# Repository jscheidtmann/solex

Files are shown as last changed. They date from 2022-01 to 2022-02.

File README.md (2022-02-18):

# Build Report for a Sol'ex Spectroheliograph
by Jens Scheidtmann

## Introduction
Christian Buit created a Do-It-Yourself 3D-print spectroheliograph, see its presentation and build instructions here:
http://www.astrosurf.com/solex/sol-ex-presentation-en.html. 

This build-log reports on my attempt at building it in the form of a diary. I hope this will be useful for others, so that my 
experience will help others. 

### License

This work is licensed under the Creative Commons Attribution-ShareAlike 4.0 International License. See file LICENSE for details.

## Building the Sol'ex

### 2022-01-12
The Shelyak kit arrived: Got the lenses, the diffraction grating, the slit and additional items for building a Star'ex. 
It's the [kit from Shelyak](https://www.shelyak.com/produit/es0027-solex-and-starex-optical-kit/?lang=en).

M3 and M4 Screws are on the way. I ordered sets of M3 and M4 screws from 4 mm length up to 40 mm length and some 
additional larger washers. Mold insert nuts are M3 and M4 from Ruthex. Unfortunately I couldn't find a bill of material 
on the original site.   

Hopefully one roll of PETG
[black filament from dasfilament](https://www.dasfilament.de/filament-spulen/petg-1-75-mm/158/petg-filament-1-75-mm-schwarz?c=21) 
is enough.

Note: Later on it turned out that a two 50mm M4 screws are necessary. 

### 2022-01-13
Read the DADOS Tutorials by [Bernd Koch](http://astrofoto.de/german/profil/fprofil.htm) available [here](https://www.baader-planetarium.com/de/blog/neue-tutorials-fuer-den-dados-spaltspektrografen/) on Baader's site (in German, english version available [here](https://www.unitronitalia.com/schede/Baader-Dados-tutorial.pdf - very slow download). Ordered a MegaMan lamp for callibration purposes.

### 2022-01-14
Ordered two [helical ZWO focusers](https://www.astroshop.eu/focusers/zwo-helical-focuser-1-25-/p,63166) and a T2-1.25" adapter.

### 2022-01-16
Conducted first prints with the PETG filament on a Flashforge Finder. The PETG is much more prone to warping, i.e. a raft and 
glue is mandatory. Hopefully I can print the large spectrometre body parts with-out too much warping.

These are the settings I used in FlashPrint 5.2.1: 
 - Extruder Temp: 230°C
 - Shells: 3
 - Infill: 60%
 - Infull-Type: Hexagons
 - Activate Raft: Yes  (used the other default settings) 

Today's printed parts (named as given in [this picture](http://www.astrosurf.com/solex/images/image-collee-701-1.webp)):
 - Interface tel. #1 (My T2-1.25" adapter fits snuggly, even on the first warped print)
 - Support fente #2
 - Bague collimateur #5
 - Support réseau #9
 - Patte réseau #10
 - Bague objective #11
 - Bague épaisseur #13
 - Raidisseur #14

Here's a picture of the parts:

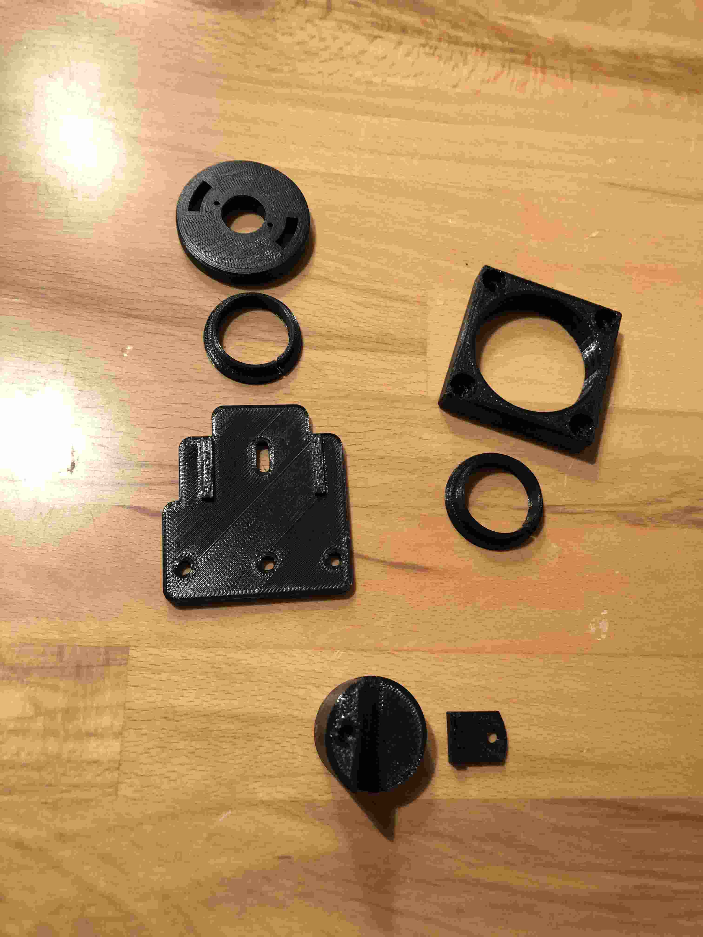
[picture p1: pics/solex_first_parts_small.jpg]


We will see, if I need to reprint the rings (#5 and #11) as they have a little bit of warping.

The STL-files are [available on github](https://github.com/Vdesnoux/Sol-ex) and there are some extensions available in subdirs:
 - motorisation_fichiers, move the diffraction grating with a motor
 - cache_parasite, avoid scattered light in the sprectrometre body
 - vernier_reseau, a dial for more visually selecting the color that is centered in the cam. Couldn't find the print-out for that, yet.

There is also a mailing list (french mostly): https://groups.io/g/Solex-project, on which new developments/extensions are reported.

### 2022-01-17
Printing the upper body part. Unfortunately this large element experienced some warping. Fortunately, the body is large enough, so that the optical path is not affected by the warping. 

### 2022-01-18
Printing the lower body part. I made especially sure that a good layer of glue is present on the 3D-printing bed. 4 hours into the printing, one edge of the body had disconnected from the bed and warping developed, which is similar to the upper body part printed yesterday. Hopefully I am able to account for the warping with the screws. If needed, I will have to print something so that the "Radisseur" (stiffener) plate is at its expected position. 

Here are pictures of both parts, so you can see the warping:

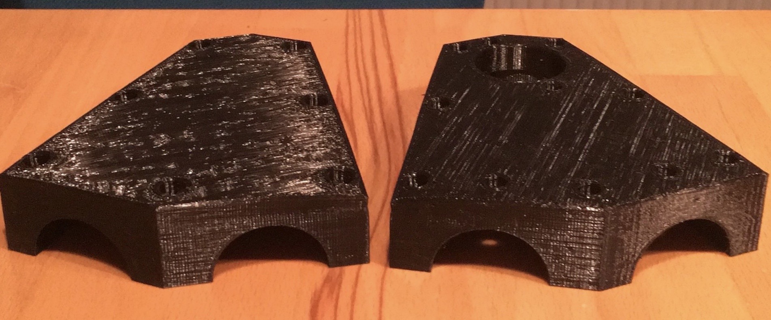
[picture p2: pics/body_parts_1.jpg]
Picture of body parts with warping ()
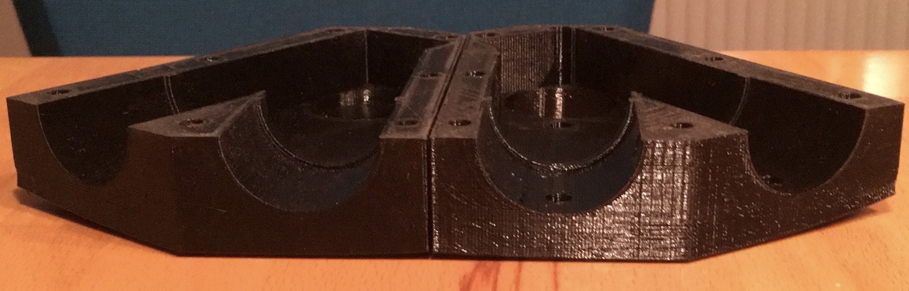
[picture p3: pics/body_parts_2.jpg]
Picture of body parts with warping ()
  

### 2022-01-19
Printed the two tubes (#4 and #12) and the collimator block (#3). The helical focusers and the T2-adapter arrived. Now everything is there to finish the Sol-ex.

The grating holder did not fit into the body part, so I had to sand the opening and the grating holder. I also sanded the body parts where they are in contact, in order get a tight fit. The T2-adapter fits nicely into the interface (#1). I printed it with-out raft (and it had no warping) and with normal layer thickness.

So far I was unable to fit the focuser on the respective tube (#12). I should have printed it in "fine" setting, but did use the normal setting, as the T2 adapter fitted perfectly in part #1. The problem is that the tube-thread does not grip the thread in the focuser. Or when it does, it's only one side of the tube and the tube gets stuck after a couple of degrees. I will reprint this one using "fine" layer thickness and probably use another slicer that randomizes the start point of outer layers. Hopefully this will be finished tomorrow. I will not use a raft, but then may have some elefant foot, which I should be able to cure with a bit of sanding.

Using the candle method I installed all Ruthex M4 and M3 threaded inserts in the body parts. A few seconds in the candle was enough. 
Some screws in the area where warping occurred could not be pushed fully in. As the screws are anyway pulling them further in, probably no problem. 

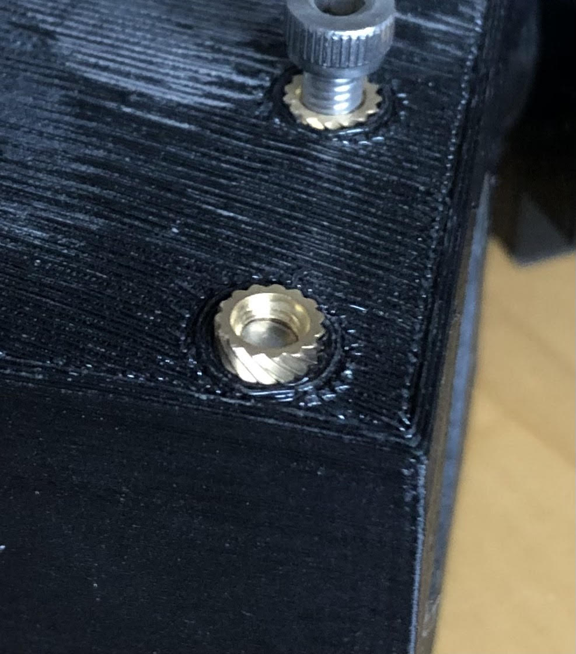
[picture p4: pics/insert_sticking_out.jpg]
Threaded insert sticking out


The collimator block needs a tad more sanding on the telescope side, as a slight warping is present. I also need to sand the tube to make it fit in the openinig of the collimator block. The slit holder will need the same treatment. 

Assembled the grating. The holder is a snug fit for the grating: I had to apply quite some force to fully place it on the holder.
I had to press a bit to get it down all the way.

### 2022-01-20
Printed the tube for the camera end: no raft, fine layer setting. Did not randomize start points.
I tried to print the disk to rotate the grating (#8). Unfortunately the infill set-up has been destroyed (or there's a bug in the slicer or, worst case, there's some dirt in the nozzle) and the disk has been printed with-out infill. So will need to repeat that tomorrow.

Sanded collimator block and slit holder. Now they fit easily into each other. Mounted the slit on the holder and the holder in the collimator block. I first tried using washers, but that didn't work out well. I should have watched the video, where no washers are present. 
 
The tube for the camera still does not fit nicely into the thread of the helical focuser. After half an hour of trying to get the tube in, I printed [a centering piece](pics/centering_piece.stl) (click to download STL) to contrain the axis and get it easier on the focuser ([3D model is here](pics/centering_piece.stl), original is [here on onshape](https://cad.onshape.com/documents/316c2c867ffea37441e19b92/w/02e4e45af20289e9be0c906b/e/80cd2974380ce7f4b167423d) - you need an account).

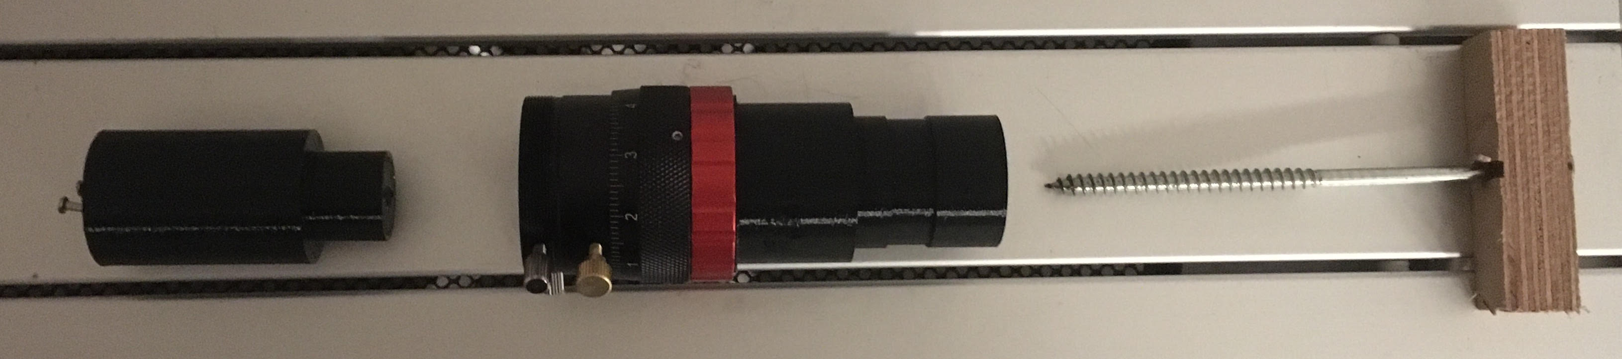
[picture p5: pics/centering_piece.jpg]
Center piece usage


Place the centering piece in the hole of the optical tube, then fix it to the tube with a piece of wood and a screw long enough (see picture). Then place this in the ZWO helical focuser and the thread of the tube is constrained to be parallel to the focuser's thread. Or put differently: The optical tubes axis and focuser axis will be held parallel by the centering piece. Apply some force to get the threads grip each other and then screw it in. In the end I used a pipe wrench to screw it all in, because it was really slippery in my hands and I was not able to create the needed torque. Then remove the screw with the wood and remove the centering piece (this is the state the picture shows). In my case, I did not make the 1.25" inch part long enough and it started turning in the focuser. I fixed that using two nails (note: the STL has been fixed to be longer, so you can grip it by hand or with a wrench).  

Looks like a "first light" is possible tomorrow. Keep your fingers crossed.

### 2022-01-21

Printed the disk for turning the grating. Assembled the lenses into the tubes. Used my 20mm cross-hair eye piece for collimating the slit-side. Unfortunately there's fog outside and I could not use objects from a real distance for fixing the focus. I therefore may need to repeat the procedure when the weather is better. 

The picture of the slit is completely off-axis. Turns out, that the warping is much heavier than expected. 

### 2022-01-22

Weather is still foggy but got a bit better than yesterday. So 1-2 km has to be infinite enough for the moment..
Recollimated the device using this setting.

Determined the warping: Taking the surface, where the two body parts touch each other as a reference line, the height of the wall on the telescope side has a difference of approximately 1.2mm and the wall thickness of the hole differs by another 0.3mm. I decide to print a wedge, that I'll glue on the body part under the turning wheel. That way the image slit should be centered again. As the turning wheel will have 3 points it is resting on, this should be stable, once the position of the grating is fixated using the screws.

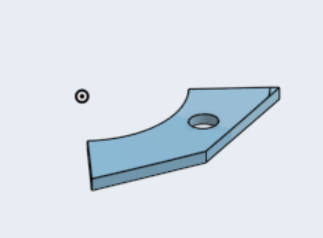
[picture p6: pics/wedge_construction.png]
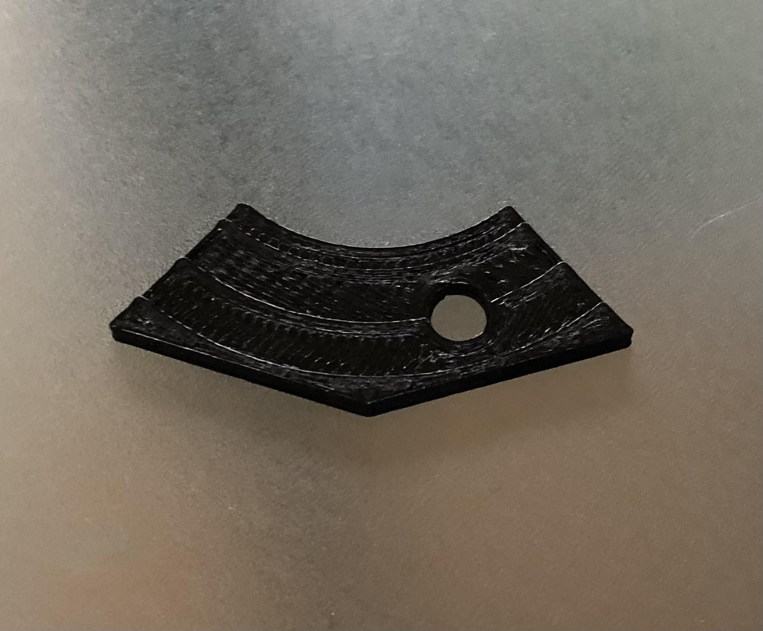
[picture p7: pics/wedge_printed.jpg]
 

I printed 5 of these wedges with different heights and settled on the slimest one. Looks good now in the crosshair eye piece (sorry, taken with cell phone, the cross-hair center should be roughly at the middle of the slit):

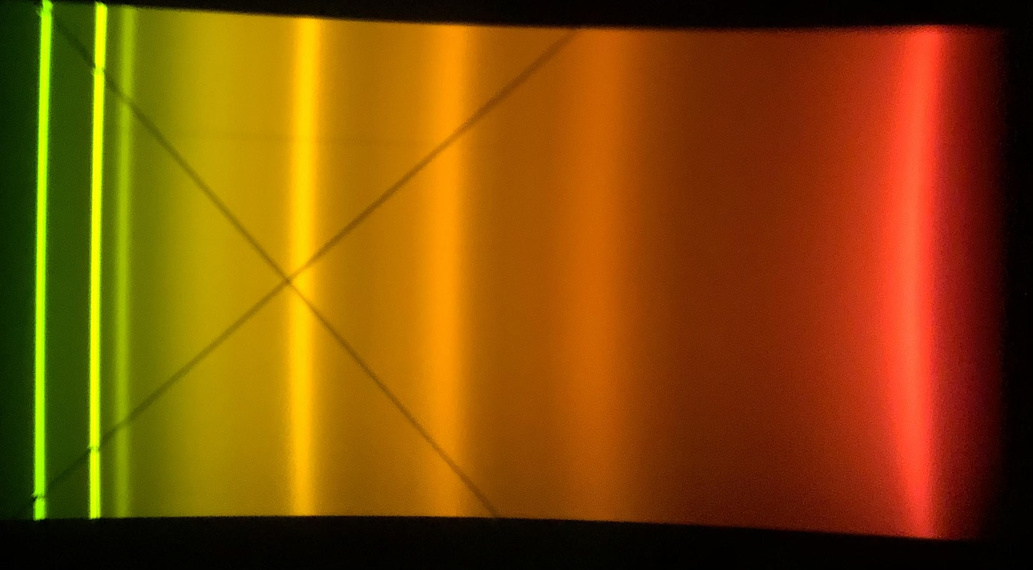
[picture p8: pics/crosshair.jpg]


My ASI224mc now gets some high resolution images of the Na-doublet(?):

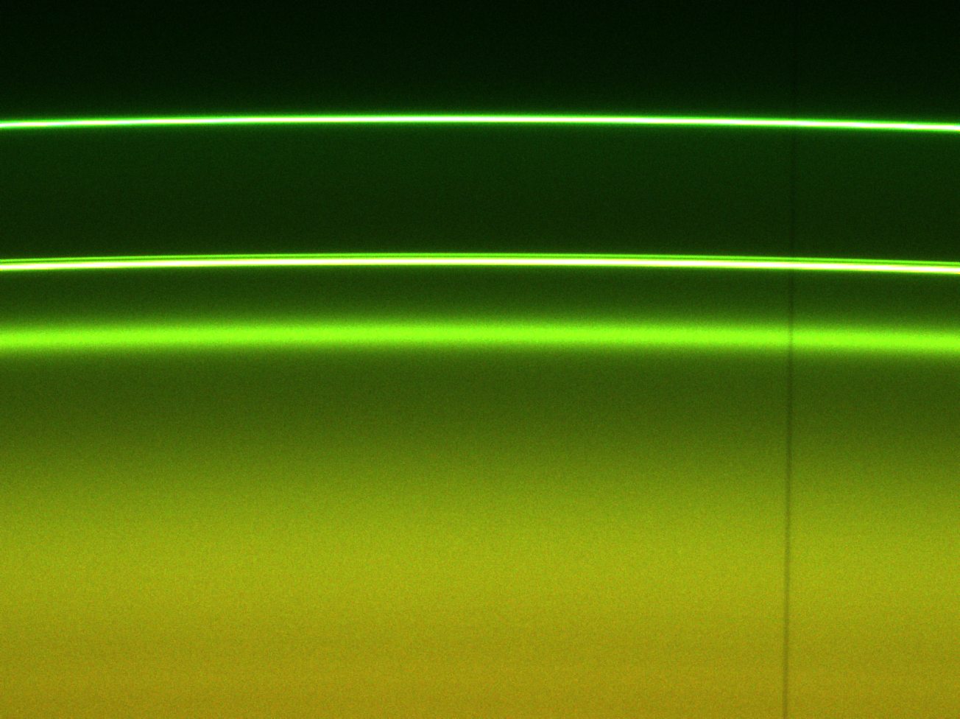
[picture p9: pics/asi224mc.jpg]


This is the device built, it weights 750g (including camera): 

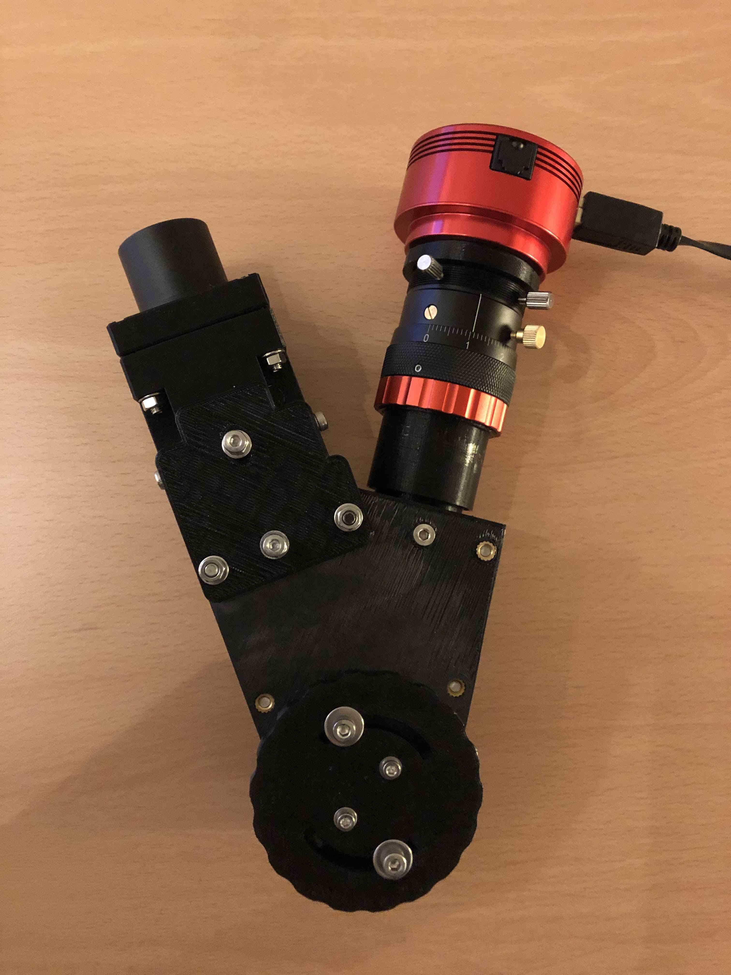
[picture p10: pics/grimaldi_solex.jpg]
Grimaldi's Sol'ex


┏(-_-)┛┗(-_- )┓┗(-_-)┛┏(-_-)┓

TODO:
 - Re-Check collimation when the weather is better.
 - Re-Check orientation of slit and camera.
 - Capture a solar video and try INTI.

## Cameras and focal lengths

This is a summary of the cameras, sensor sizes and recommended focal lengths, summed up from the [construction page](http://www.astrosurf.com/solex/sol-ex-construction-en.html):

| Camera | Sensor | Sensor Size | Sensor Dimensions / mm² | Pixel Size / µm | Resolution / Å/px | Max Focal Length / mm | Slit/Cam Limited | Tube mod | 
|:----------|:-----------:|:------:|:---------:|----:|------------:|-------:|:------|:--:|
| ASI178mm  | Sony IMX178 | 1/1.8" | 7.5 x 5.0 | 2.4 | 0.0626 | 480 | ideal | No |
| ASI290mm  | Sony IMX290 | 1.3" | 5.6 x 3.2 | 2.9 | 0.0726 | 380 | Cam | No |
| ASI174mm  | Sony IMX174 | 1/1.2" | 11.3 x 7.1 | 5.86 | 0.1440 | 480 | Slit | No |
| ASI183mm  | Sony IMX183 | 1"     | 13.2 x 8.8 | 2.4 | 0.0626 | 480 | Slit | No |
| ASI294mm  | Sony IMX294 | 4/3"   | 19.1 x 13.0 | 4.63 |  0.0604 | 480 | Slit | No |
| ASI6200mm | Sony IMX455 | full frame | 36 x 24 | 3.76 |  1.028 | 480 | Slit | Yes (short) |
| Sony Alpha DLSR | Sony  | full frame | 36 x 24 | 8.7 |  -/- | -/- | -/- | Yes (APN) |
| ASI224mc  | Sony IMX224 | 1/3"   | 4.9 x 3.7   | 3.75 | -/- | 300? | Cam | No | 

Note: The entrance slit is 4.5mm long. 
See: https://en.wikipedia.org/wiki/Crop_factor for a comparison of sensor formats

## 2022-01-22

I recollimated the camera side with an object on the horizon and across the city (4 km). Now when trying to collimate 
the slit-side, it turns out that the collimator block needs to go in a few more millimeters. I use Forstner drills 
to remove a bit of the outer layers and then are able to get it in focus/collimation. My Sol'Ex is not collimated 
and ready to go. 

## 2022-01-23

I add a print-out of the colors on the Sol'Ex body: You can download a png file for the 2400 l/mm grating here:
https://groups.io/g/Solex-project/topic/81036290#433

## 2022-01-27

Using long exposure times, I collect an example spectra of Mg triplet lines (with clouds):

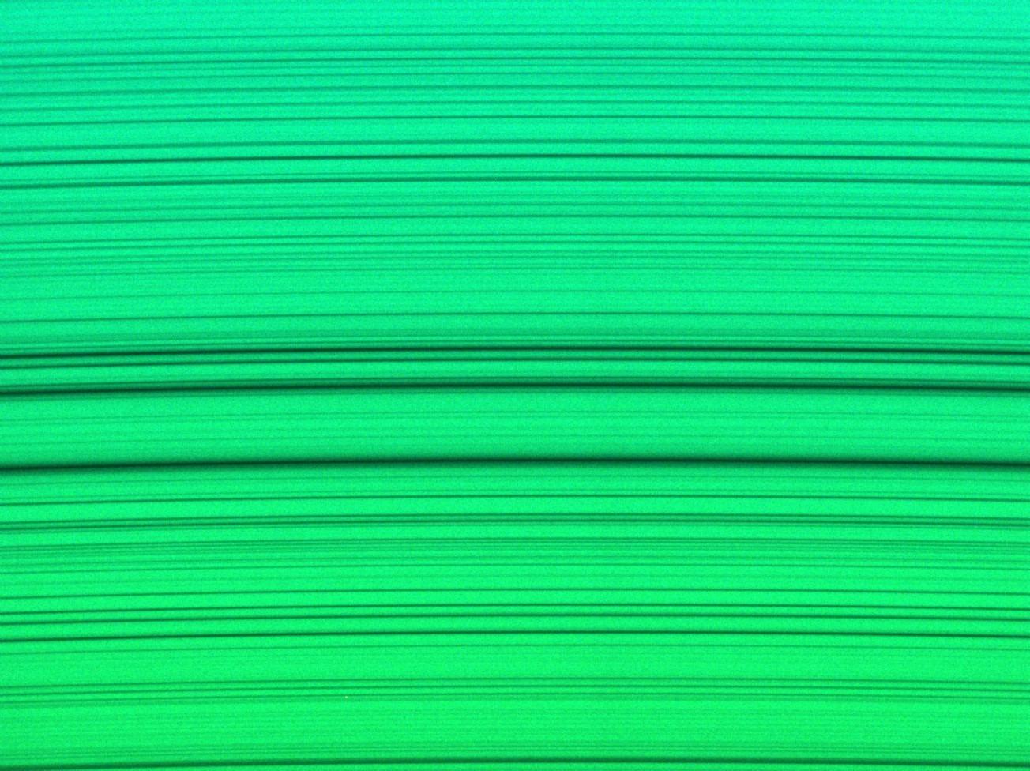
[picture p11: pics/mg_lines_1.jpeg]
Sol'Ex showing Mg Lines
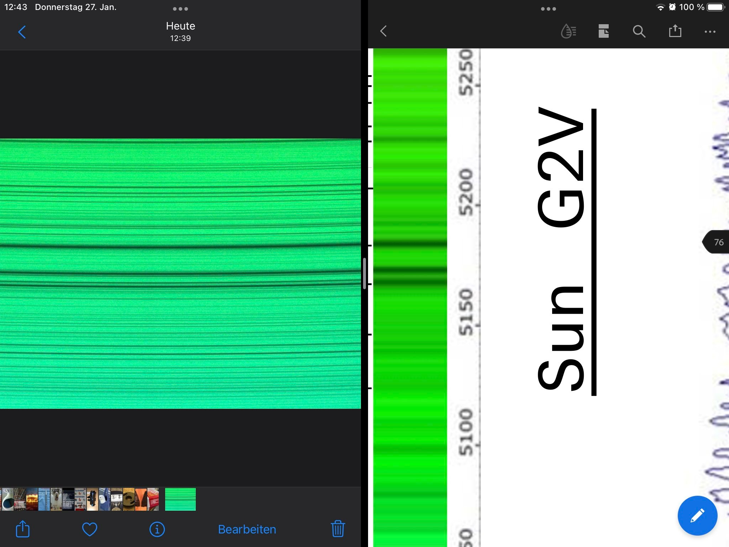
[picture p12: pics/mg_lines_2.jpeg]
Comparing previous picture to sun spectrum


The spectral resolution is awesome!

I read a bit on the Sol'Ex groups.io and discover an Excel/Calc sheet for the geometry. It can be downloaded from this link
into the groups.io archive: https://groups.io/g/Solex-project/topic/80304988?p=Created%2C%2C%2C20%2C2%2C0%2C0
It is called: "SimSpec_SHG V1.3"

## 2022-01-28

I attach my Sol'Ex to a William Optics "Uniguider" 50/200 (f/4) and use this to capture my first image of the sun. 
It turns out that I have to use the smallest exposure times that my ASI224mc is capable of. I recognize too late, that 
Christian uses a Herschel wedge in his videos. Fortunately my cam and the Sol'Ex are not damaged. 

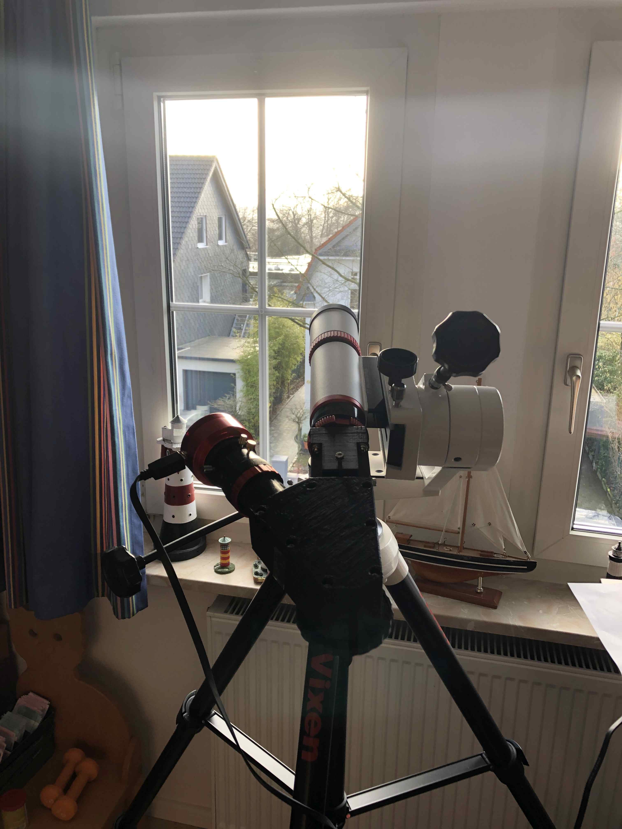
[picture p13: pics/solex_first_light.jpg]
Sol'Ex having first sun light
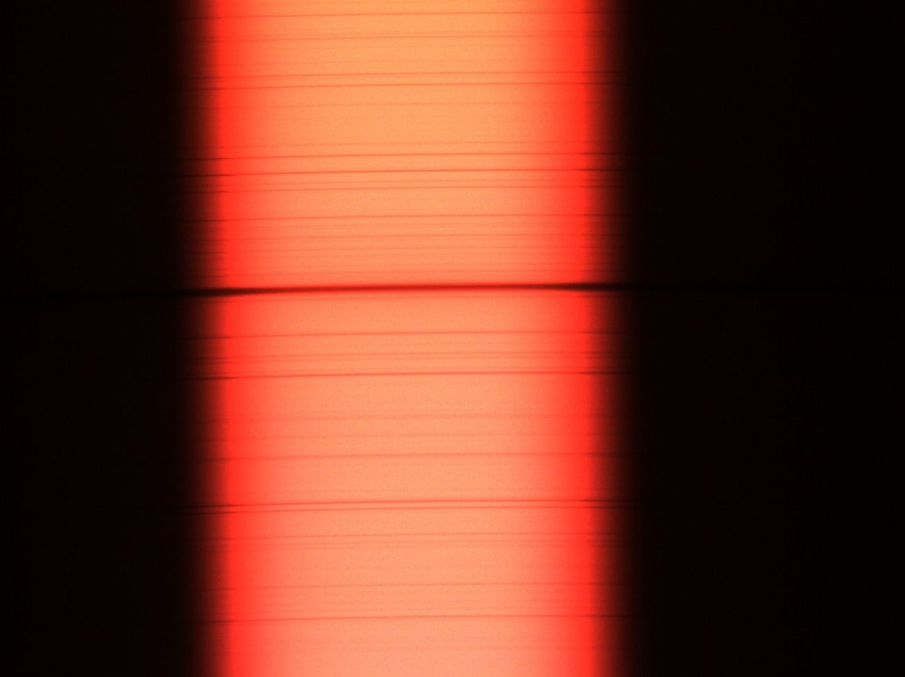
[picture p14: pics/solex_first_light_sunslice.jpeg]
a slice of the sun seen in Sol'Ex


I am not able to focus the telecope correctly, as after 30 min clouds come in. 

## 2022-01-29 -- 2022-02-17

I create a sun screen from [Baader AstroSolar® Safty Film 5.0](https://www.baader-planetarium.com/en/solar-observation/astrosolar-viewers-and-film/astrosolar-safety-film-od-5.0-(20x29-100x50-117x117-cm).html) 
with 50mm diameter, but it turns out, 
that this is too much intensity reduction and one cannot get acceptable exposure times.  

I [design](https://cad.onshape.com/documents/316c2c867ffea37441e19b92/w/02e4e45af20289e9be0c906b/e/fcda335b8769b052544592b2) and print a diaphragm, that stops down to f/10:

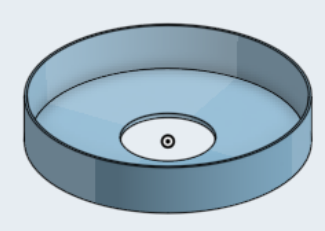
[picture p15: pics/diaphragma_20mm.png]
Diaphragma 20 mm diameter


Due to bad weather, I am not able to test it out. 

## 2022-02-18

The last few week's weather has been awful: Mostly cloudy, sun not even visible, only a few days with a few hours 
of sun (and then fast moving clouds). Going outside with the family took precedence. Yesterday and today Europe is hit by storms.

In between I printed a holder/adapter for the calibration lamp:

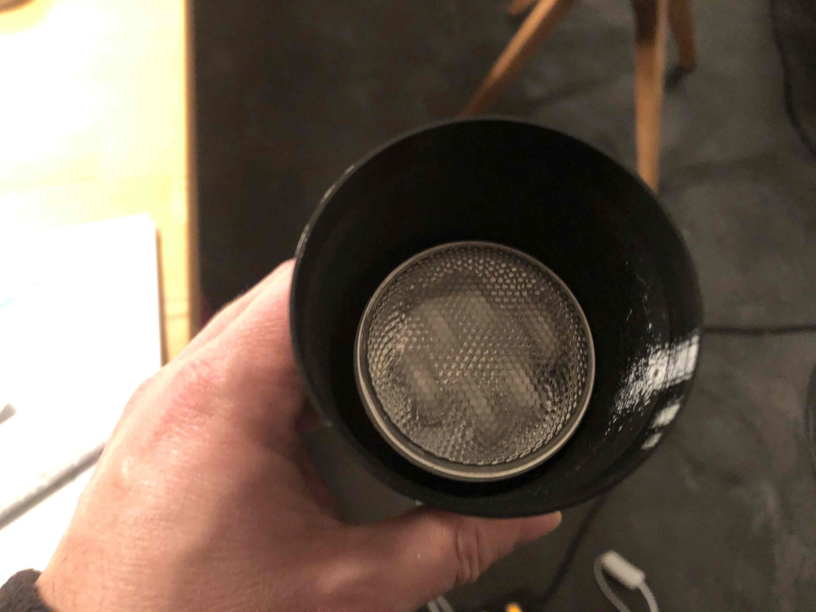
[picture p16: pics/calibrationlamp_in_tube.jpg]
Calibration lamp in tube
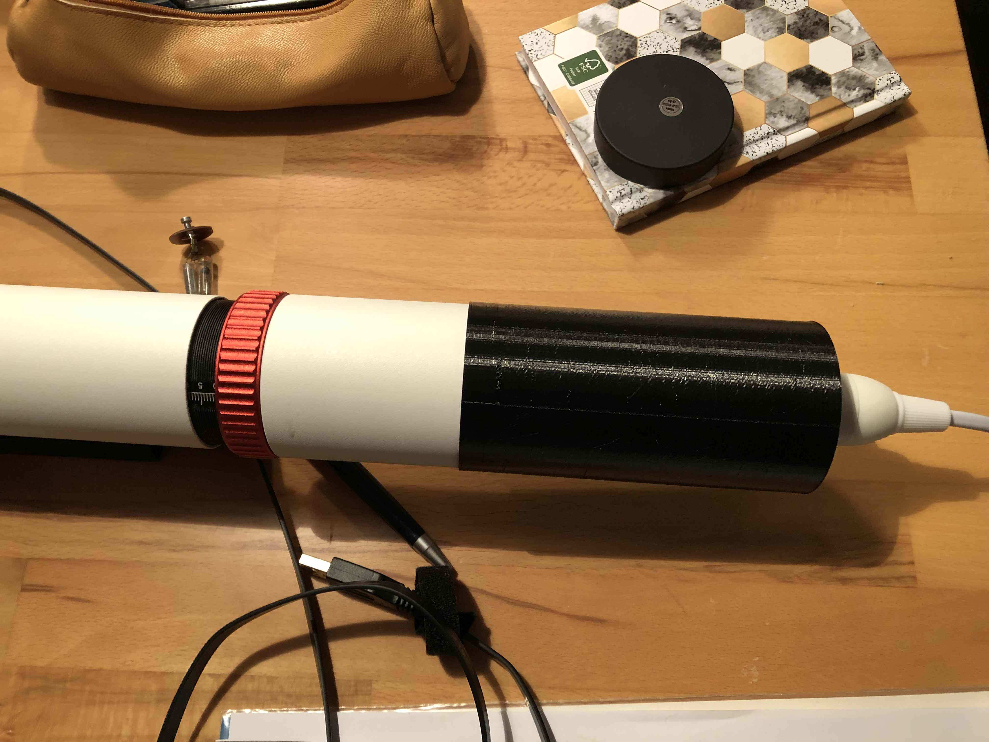
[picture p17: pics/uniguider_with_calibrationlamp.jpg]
Calibration lamp tube attached to telescope


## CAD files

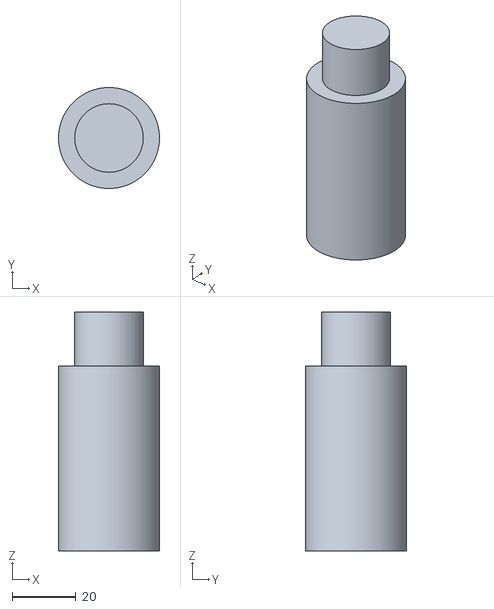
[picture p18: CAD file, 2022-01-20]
pics/centering_piece.stl
31.7 x 31.7 x 75.0

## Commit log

2022-01-20 3D files for centering piece
    [centering_piece.stl]
2022-01-22 Added pic of insert that is sticking out.
2022-01-22 Fix image display (insert)
2022-01-22 Show device
2022-01-22 Table summary of cameras
